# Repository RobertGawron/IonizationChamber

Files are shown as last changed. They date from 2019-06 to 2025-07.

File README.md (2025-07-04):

# Ionization Chamber (a device for measuring radioactivity levels)



## Objective

There are many ionization chamber projects online, but most (though not all) produce false positive results. It's cool when a radioactive sample is placed near the detector and the detector shows an increased radiation value, but then, if you place your hand or any non-radioactive object nearby, the readings are high too. This is because, due to high amplification, these devices pick up a lot of noise, making the measurements unreliable.

This project aims to address and eliminate this issue.

## Principle of operation

An ionization chamber is a type of radiation detector that measures ionizing radiation by detecting the charged particles (ions) produced when radiation interacts with the gas inside the chamber. The basic working principle relies on the ionization process. 

* **Radiation Interaction:** When ionizing radiation (such as alpha, beta, or gamma radiation) enters the chamber, it interacts with the gas inside, typically air. This interaction causes the gas molecules to become ionized, producing free electrons and positive ions. 
* **Electric Field:** The chamber contains two electrodes: a central anode and a surrounding cathode. A high voltage is applied between these electrodes, creating an electric field inside the chamber. 
* **Ion Collection:** The free electrons, which are negatively charged, are attracted to the positive anode, while the positively charged ions are attracted to the cathode. As these ions move toward the electrodes, they create an electrical current. 
* **Current Measurement:** The generated current is directly proportional to the number of ions produced, which in turn is related to the amount of radiation that has passed through the chamber. This current is then measured and used to calculate the intensity of the radiation.

Below is an image of the device that was assembled and tested (hardware revision 4.0). Since then, a new version has been developed but has not yet been tested. This repository, in its current state, represents the latest version. For details on the tested version, [refer to 4.0 tag](https://github.com/RobertGawron/IonizationChamber/releases/tag/4.0).  

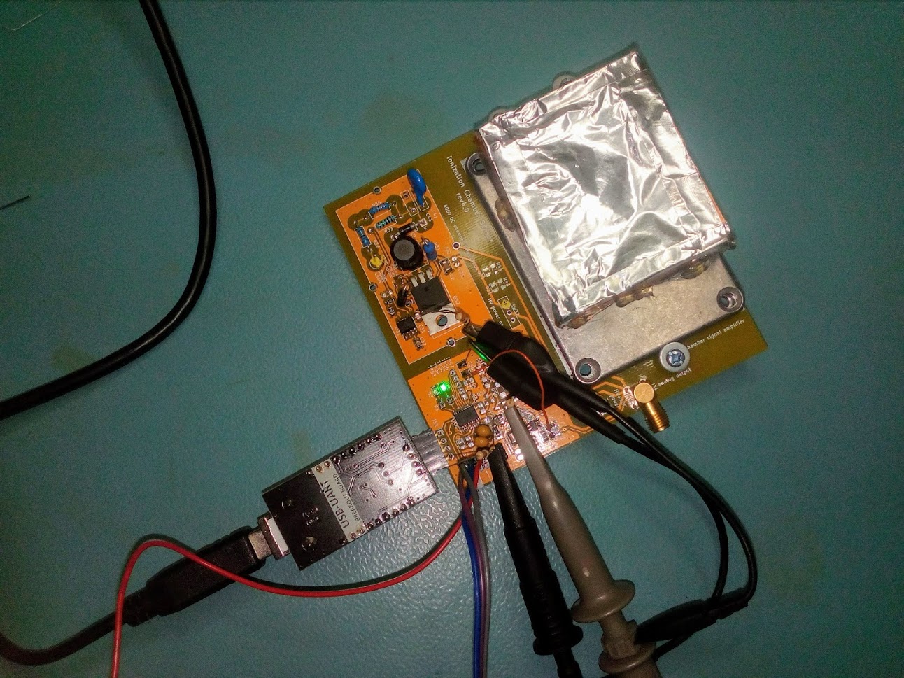
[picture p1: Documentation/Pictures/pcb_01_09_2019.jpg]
picture of device


## System architecture

It is designed in a way that the device can work remotely, e.g. no connection via USB cable to user’s PC is needed.



Remarks:
* The amplifier has three stages (the first stage is a transimpedance amplifier, not a FET transistor like most projects use).
* The ionization chamber is polarized with three 12V batteries connected in series.

## Hardware

PCB was done in KiCAD.

### Hazards

* **The battery container electrodes for chamber polarization are very close to the metal casing; the soldered electrodes should be filed down and secured with insulating tape to prevent short circuits.**
* **The device uses relatively high voltage (32V) to polarize the ionization chamber.** The electrodes of the ionization chamber should not be touched.

## Software

Measurements are collected from the COM port (tunneled over USB) by a Python script and stored in a .csv file. This file can later be parsed using R scripts to generate various diagrams, such as radioactivity changes over time, radioactivity histograms, and box plots for different samples.

measurement data flow diagram

* [Details about the firmware are available here.](./Software/Firmware/README.md)
* [Details about the acquisition software are available here.](./Software/MeasurementAcquisition/README.md)
* [Details about the measurement processing software are available here.](./Software/MeasurementAnalysis/README.md)

In the future, data from the device will be gathered and processed using the [HardwareDataLogger project](https://github.com/RobertGawron/HardwareDataLogger), which is currently in development.

## Simulation

A simple mockup was created to generate dummy test data without the need for the real device. This allows testing of the acquisition software (mainly the scripts that generate output diagrams) without requiring hardware.

[More details.](Simulation/README.md)

## DevOps

All software is developed inside a Docker container.

[More information about setting up the environment.](./Documentation/Manuals/README.md)

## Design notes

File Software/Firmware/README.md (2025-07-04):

# Architecture

Below is the sequence diagram for the firmware.

firmware main sequence diagram

firmware tick sequence diagram

# Building Firmware

Docker is used to create an isolated and reproducible work environment.

[Detailed information about setting up the environment.](../../Documentation/Manuals/README.md)

# Protocol for sending measurements via UART

## Purpose

To ensure data integrity when sending information from the ionization chamber device to the computer, a simple protocol was added to encapsulate each data or command transmission.

## Protocol details

### Definition of the message

uart frame format diagram

The field “msg length” describes the number of bytes in the “data” section.

The content of the data section in the above message is an example and may vary depending on the message ID. Currently, only one message is supported, as shown above.

### Defined message ids and message content

Currently, only one message type is defined (with ID = 1).

* Msg ID: 1 - Data from the last analog measurement of the actual value.
Msg Data Section:
    * ADC configuration
    * MSB (most significant byte) from ADC
    * LSB (least significant byte) from ADC

### CRC

The CRC is calculated by XOR-ing all bytes in the "preamble" and "data" sections.

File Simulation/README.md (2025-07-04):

# Simulation

## Purpose

This simulation spits out .csv files filled with random values that mimic a real device sending measurements to the PC over UART. It lets us exercise the data-processing scripts without having the actual hardware on hand.

We run the real Python application but swap in a stub for the low-level serial module. That way the identical codebase runs in both simulation and production-only the UART driver gets replaced.

# Usage

[Information on how to use this tool.](../Documentation/Manuals/README.md)

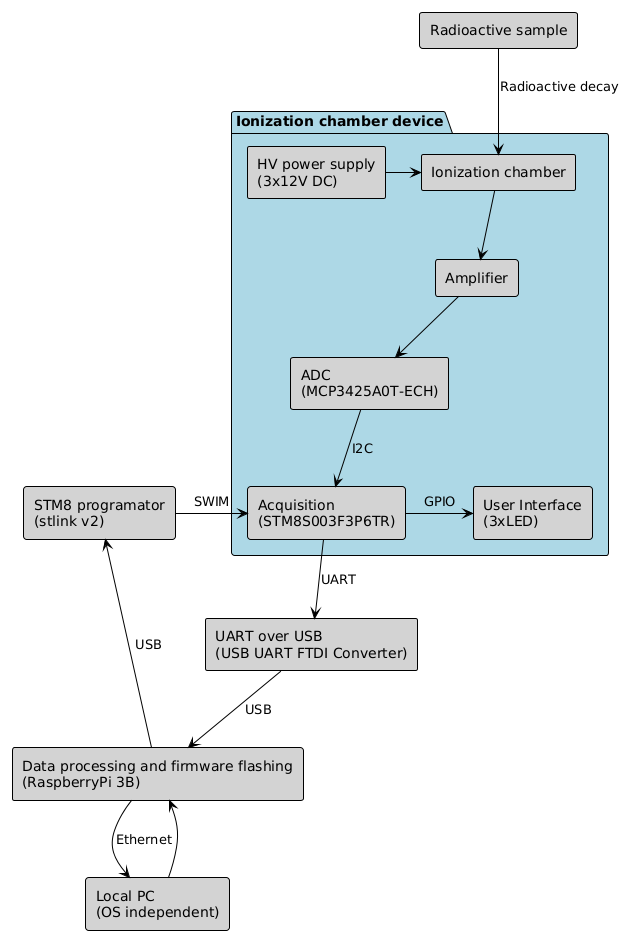
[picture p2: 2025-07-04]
Documentation/Diagrams/ArchitectureOverview-1.png

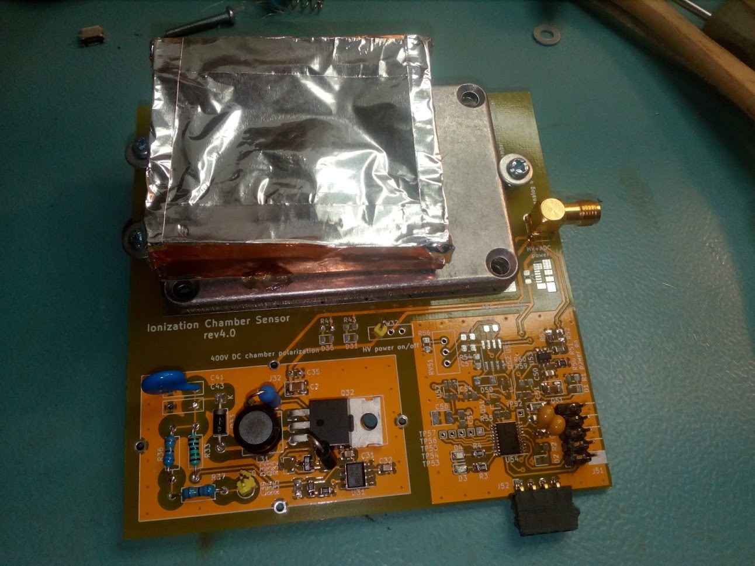
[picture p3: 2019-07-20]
Documentation/Pictures/pcb_20_07_2019.jpg

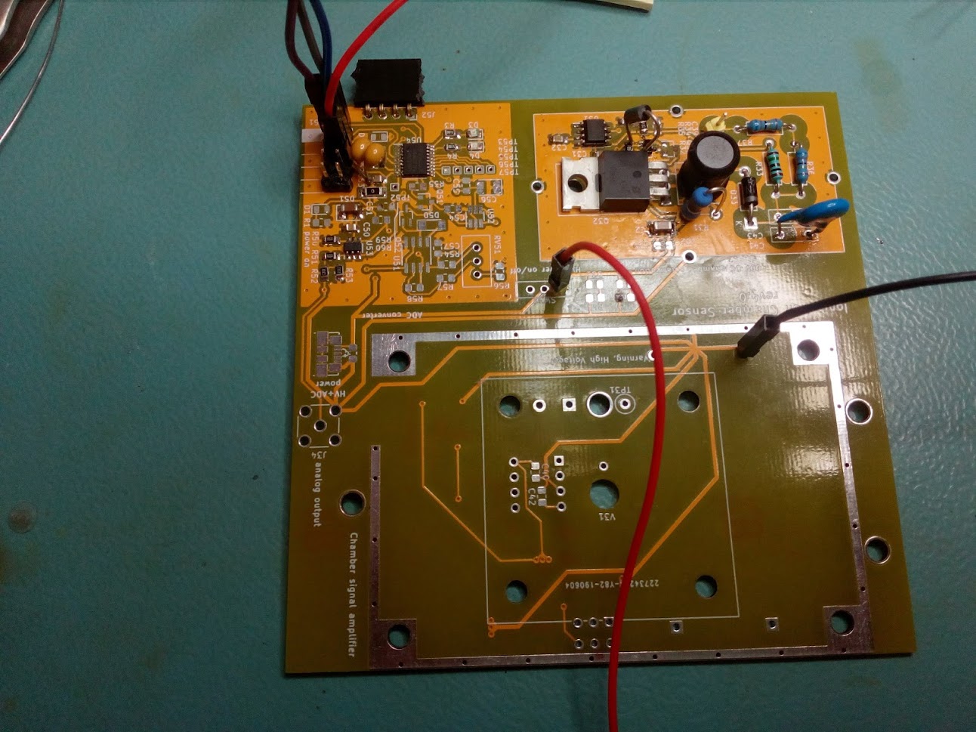
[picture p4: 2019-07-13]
Documentation/Pictures/pcb_13_07_2019.jpg

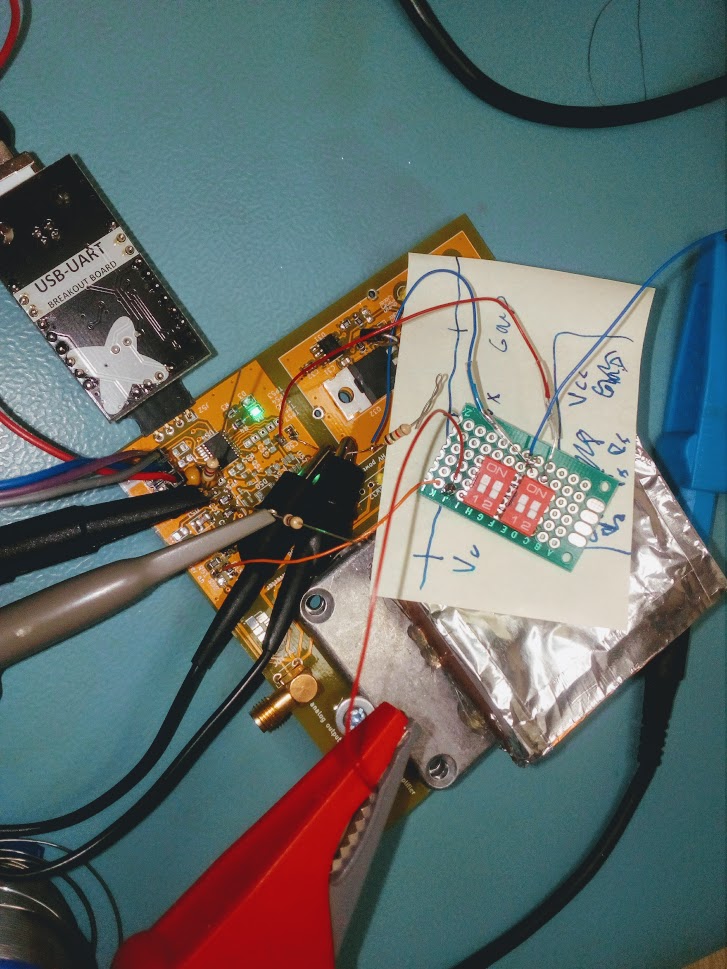
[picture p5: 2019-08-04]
Documentation/Pictures/pcb_04_08_2019.jpg

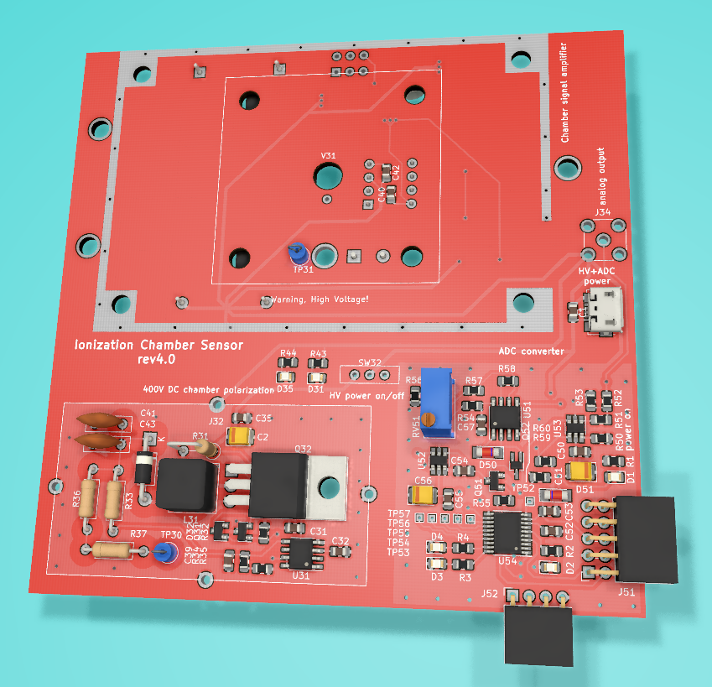
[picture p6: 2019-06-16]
Documentation/Pictures/render_26_05_2019.png

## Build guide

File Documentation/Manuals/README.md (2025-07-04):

# Toolchain

# Prerequisites

Install Docker. For Windows you need WSL installed first and some Linux image for it.

# Building, running, and stopping a Docker image

For me, using Docker in embedded systems has a key advantage: it eliminates the need for a README filled with outdated commands for setting up the development environment. In reality, such lists are rarely kept up to date (I often forget to update them myself too!). Docker solves this problem by providing a structured list of everything you need to install to get your environment up and running. But it's more than just a list - it's code, meaning it can be verified, maintained, and reused easily.

Build the Docker image by running the following command in the IonizationChamber directory. Rebuild only if the Dockerfile or docker-compose.yml changes:

docker-compose build

Start the Docker Image. Run the following command to start the Docker container:

docker-compose up -d

Log into the Docker Image:

docker-compose exec ionizationchamber bash

To log out from the Docker container, press Ctrl+D.

To stop and clean up the Docker

docker-compose down --remove-orphans

# Building firmware

Log into the Docker container (Building, running, and stopping a Docker image" section).

Run the following commands:

mkdir -p /workspace/build/firmware && cd /workspace/build/firmware 
cmake -DCMAKE_TOOLCHAIN_FILE=/workspace/Software/Firmware/sdcc-stm8.cmake -B . -S /workspace/Software/Firmware/ && cmake --build . -j$(nproc)

oneliner:

mkdir -p /workspace/build/firmware && cd /workspace/build/firmware && cmake -DCMAKE_TOOLCHAIN_FILE=/workspace/Software/Firmware/sdcc-stm8.cmake -B . -S /workspace/Software/Firmware/ && cmake --build . -j$(nproc)

The produced binary is IonizationChamber.ihx.

# Hardware flashing

For first time flashing the IC needs to be unlocked:

stm8flash -c stlinkv2 -p stm8s003f3 -u

Flashing:

stm8flash -c stlinkv2 -p stm8s003f3 -w IonizationChamber.ihx

# C Docs coverage

source /workspace/venv/bin/activate && cd /workspace/build/ && rm -rf /workspace/build/* && cmake /workspace/ && make docs

# C, Python and R Code Formatter

source /workspace/venv/bin/activate && cd /workspace/build/ && cmake /workspace/ && make style

# Firmware Unit Tests and Code Coverage

mkdir -p /workspace/build/ut && cd /workspace/build/ut
cmake -DCMAKE_BUILD_TYPE=Debug /workspace/Software/Firmware/UnitTest/
make -j$(nproc)
make run_all_tests
make coverage

oneliner:

mkdir -p /workspace/build/ut && cd /workspace/build/ut && cmake -DCMAKE_BUILD_TYPE=Debug /workspace/Software/Firmware/UnitTest/ && make -j$(nproc) && make run_all_tests  && make coverage

# C static analyze

source /workspace/venv/bin/activate && cd /workspace/build && cmake .. && make cstatic

Note: cppcheck is explicite not installed, this tool gives so much false warnings and so little actual help that it pointless to use.

# Python static analyze

source /workspace/venv/bin/activate && cd /workspace/build && cmake .. && make pystatic

# Python Unit Test and Code Coverage

source /workspace/venv/bin/activate && cd /workspace/build && cmake .. && make pycoverage

# R static analyze

source /workspace/venv/bin/activate && cd /workspace/build && cmake .. && make rstatic

# Running MeasurementAcquisition scripts

Log into the Docker container (Building, running, and stopping a Docker image" section).

Edit config.py to select the correct COM port for the Ionization Chamber.

Run the data acquisition script. It will log the Ionization Chamber's output to the screen and save it to data.csv for further processing.

python main.py

# UML generation

docker pull plantuml/plantuml-server:jetty

docker run -d -p 8080:8080 plantuml/plantuml-server:jetty

For more details:
https://plantuml.com/starting

# Simulation

source /workspace/venv/bin/activate

pip install -e /workspace/Software/MeasurementAcquisition

cd /workspace/Simulation && python3 main.py

Stop after couple of seconds by pressing Ctr+D, it will generate .cvs file with dummy data

# Credits:
* [stm8flash in Docker](https://github.com/ivankomolin/docker-stm8/blob/master/Dockerfile)

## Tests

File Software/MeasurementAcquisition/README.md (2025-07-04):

# Simulation

## Purpose

This application gathers data from the device via UART over USB and stores timestamped measurements in a .csv file for further processing.

It was developed to run on a Raspberry Pi but should work on any Linux or Windows system. One note for running it on Windows is that the name of the COM port (configured in DEVICE_ID) has a different format.

# Usage

[Information on how to use this tool can be found in the "Building, running, and stopping a Docker image" and "Running MeasurementAcquisition scripts" sections.](../DevOps/Docker/README.md)

## Architecture

The diagram below shows the **Sequence Diagram** of this application:

state diagram

Note that the application can't be stopped normally; use Ctrl+C to terminate it.

The diagram below shows the **State Diagram** of this application:

state diagram

Note that the "Failure" state is not implemented. We assume that everything works correctly all the time.

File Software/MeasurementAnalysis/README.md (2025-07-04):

# Purpose

Scripts for analyzing and visualizing radiation measurement data from ionization chamber sensor.

# Content

## Single Sample Analysis (radiation_analysis_single.R)

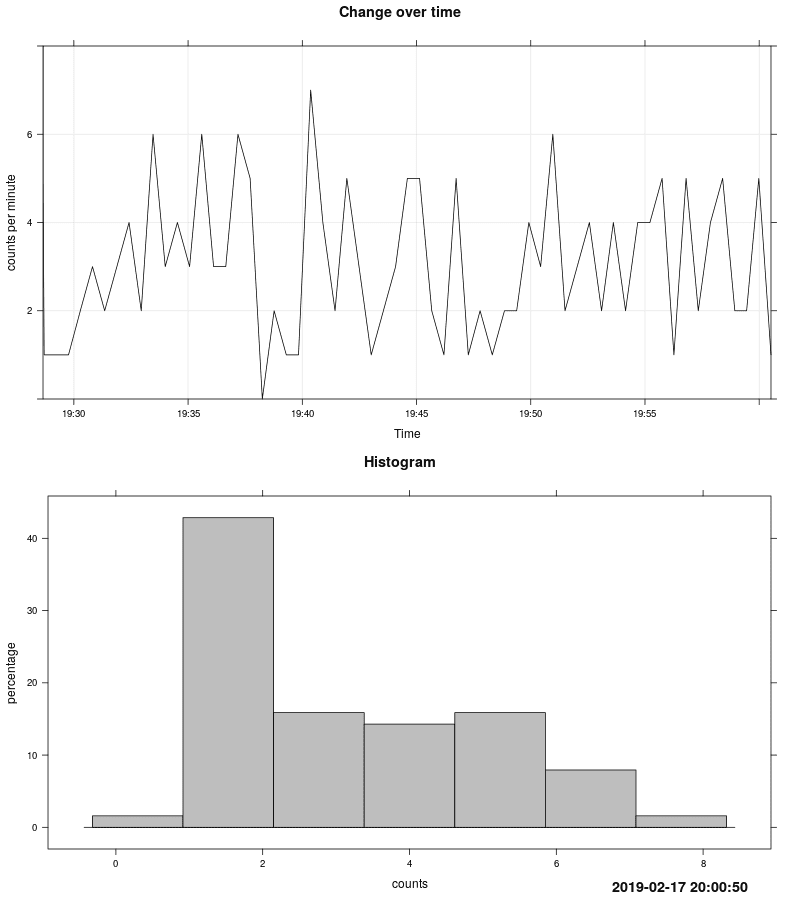
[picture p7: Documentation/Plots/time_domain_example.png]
time_domain


#### Purpose:

Analyzes a single radiation sample, producing:

Time series plot of radiation counts

Histogram of radiation distribution

#### Input

A CSV file (data.csv) with two columns:

Time: Timestamps in %Y-%m-%d %H:%M:%S.%OS format

Voltage: Measured voltage from ionization chamber

#### Output

Two image files (PNG and SVG) with the filename pattern:
radiation_analysis_single_<timestamp>.<ext>

#### Usage

Place your data in data.csv in the same directory

Run the script:

Rscript radiation_analysis_single.R

## Multi-Sample Comparison (radiation_analysis_multi.R)

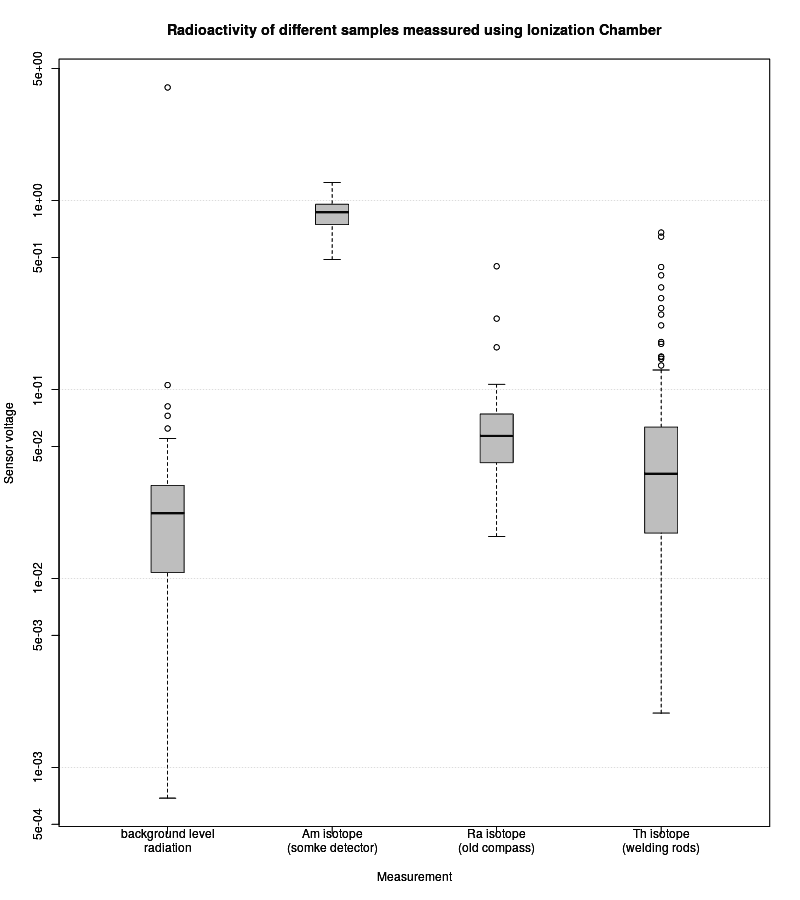
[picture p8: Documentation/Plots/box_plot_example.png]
boxplot


#### Purpose

Compares radiation levels across multiple samples using boxplots.

#### Input

Multiple CSV files (configured in the script) each containing:

Time: Timestamps (optional, used for footer)

Voltage: Radiation counts (required)

#### Output

Two image files (PNG and SVG) with the pattern:
radiation_comparison_<timestamp>.<ext>

#### Usage

Configure samples in the radiation_analysis_multi.R script (search for line shown below)

samples <- list(
  background = list(file = "DataNoSample.csv", name = "Background Radiation"),
  americium = list(file = "DataSample1.csv", name = "Am-241 (Smoke Detector)"),
  radium = list(file = "DataSample2.csv", name = "Ra-226 (Old Compass)")
)

Run the script:

Rscript radiation_analysis_multi.R

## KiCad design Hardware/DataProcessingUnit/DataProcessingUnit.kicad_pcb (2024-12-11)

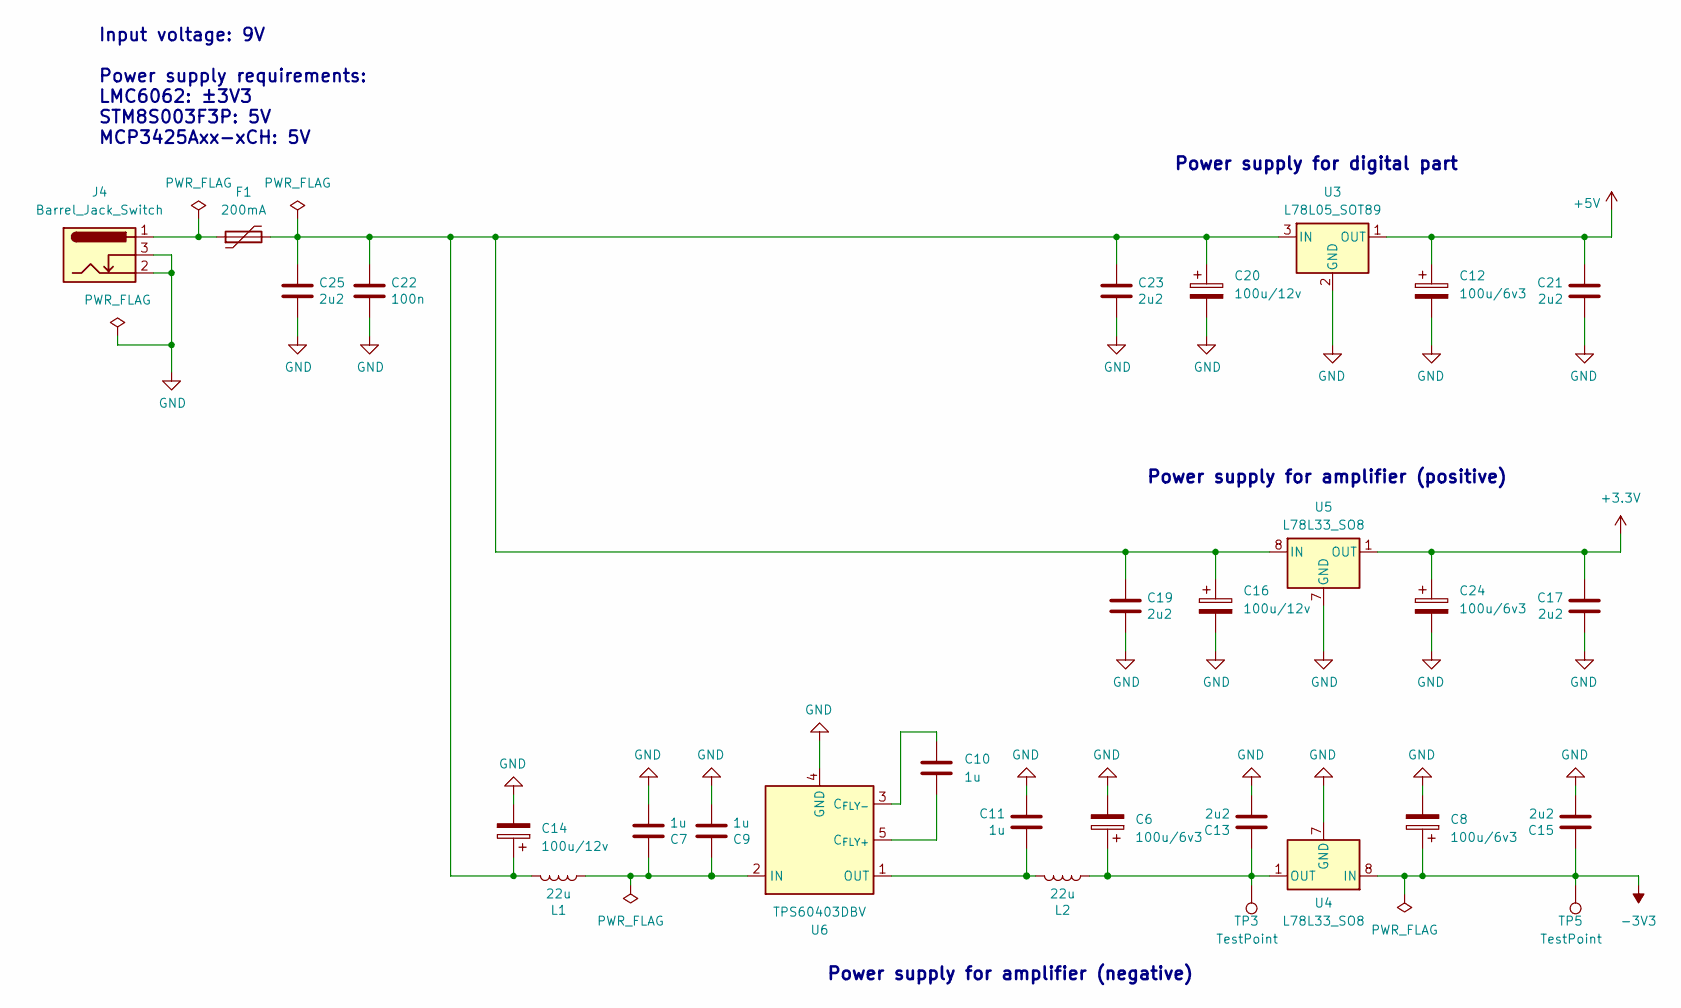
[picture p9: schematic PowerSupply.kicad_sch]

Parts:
C6, C8, C24: 100u/6v3; CP_EIA-3528-21_Kemet-B
C7, C9, C10, C11: 1u; C_0805_2012Metric
C12: 100u/6v3; CP_Elec_6.3x5.8
C13, C15, C17, C19, C21, C23, C25: 2u2; C_0805_2012Metric
C14, C16, C20: 100u/12v; CP_Elec_6.3x5.8
C22: 100n; C_0805_2012Metric
F1: 200mA; Fuse_1206_3216Metric
J4: Barrel_Jack_Switch; BarrelJack_GCT_DCJ200-10-A_Horizontal
L1, L2: 22u; L_7.3x7.3_H3.5
TP3, TP5: TestPoint; TestPoint_Pad_D1.0mm
U3: L78L05_SOT89; SOT-89-3
U4, U5: L78L33_SO8; SOIC-8_3.9x4.9mm_P1.27mm
U6: TPS60403DBV; SOT-23-5

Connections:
+3.3V: C17.1, C24.1, U5.1 (OUT); also elsewhere on the board
+5V: C12.1, C21.1, U3.1 (OUT); also elsewhere on the board
-3V3: C8.1, C15.1, TP5.1, U4.8 (IN); also elsewhere on the board
GND: C6.2, C7.2, C8.2, C9.2, C11.2, C12.2, C13.2, C14.2, C15.2, C16.2, C17.2, C19.2, C20.2, C21.2, C22.2, C23.2, C24.2, C25.2, J4.2, J4.3, U3.2 (GND), U4.2 (GND), U4.3 (GND), U4.6 (GND), U4.7 (GND), U5.2 (GND), U5.3 (GND), U5.6 (GND), U5.7 (GND), U6.4 (GND); also elsewhere on the board
unnamed: F1.1, J4.1
unnamed: C14.1, C16.1, C19.1, C20.1, C22.1, C23.1, C25.1, F1.2, L1.2, U3.3 (IN), U5.8 (IN)
unnamed: C6.1, C13.1, L2.1, TP3.1, U4.1 (OUT)
unnamed: C10.2, U6.5 (C_{FLY+})
unnamed: C10.1, U6.3 (C_{FLY-})
unnamed: C7.1, C9.1, L1.1, U6.2 (IN)
unnamed: C11.1, L2.2, U6.1 (OUT)

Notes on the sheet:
Power supply for amplifier (negative)
Power supply for amplifier (positive)
Power supply for digital part
Input voltage: 9V Power supply requirements: LMC6062: ±3V3 STM8S003F3P: 5V MCP3425Axx-xCH: 5V

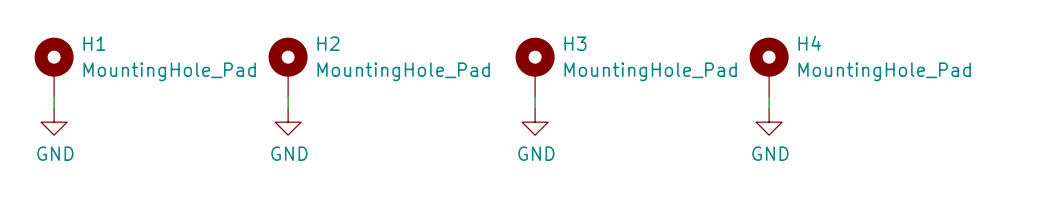
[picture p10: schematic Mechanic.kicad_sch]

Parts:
H1, H2, H3, H4: MountingHole_Pad; MountingHole_3.5mm_Pad

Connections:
GND: H1.1, H2.1, H3.1, H4.1; also elsewhere on the board

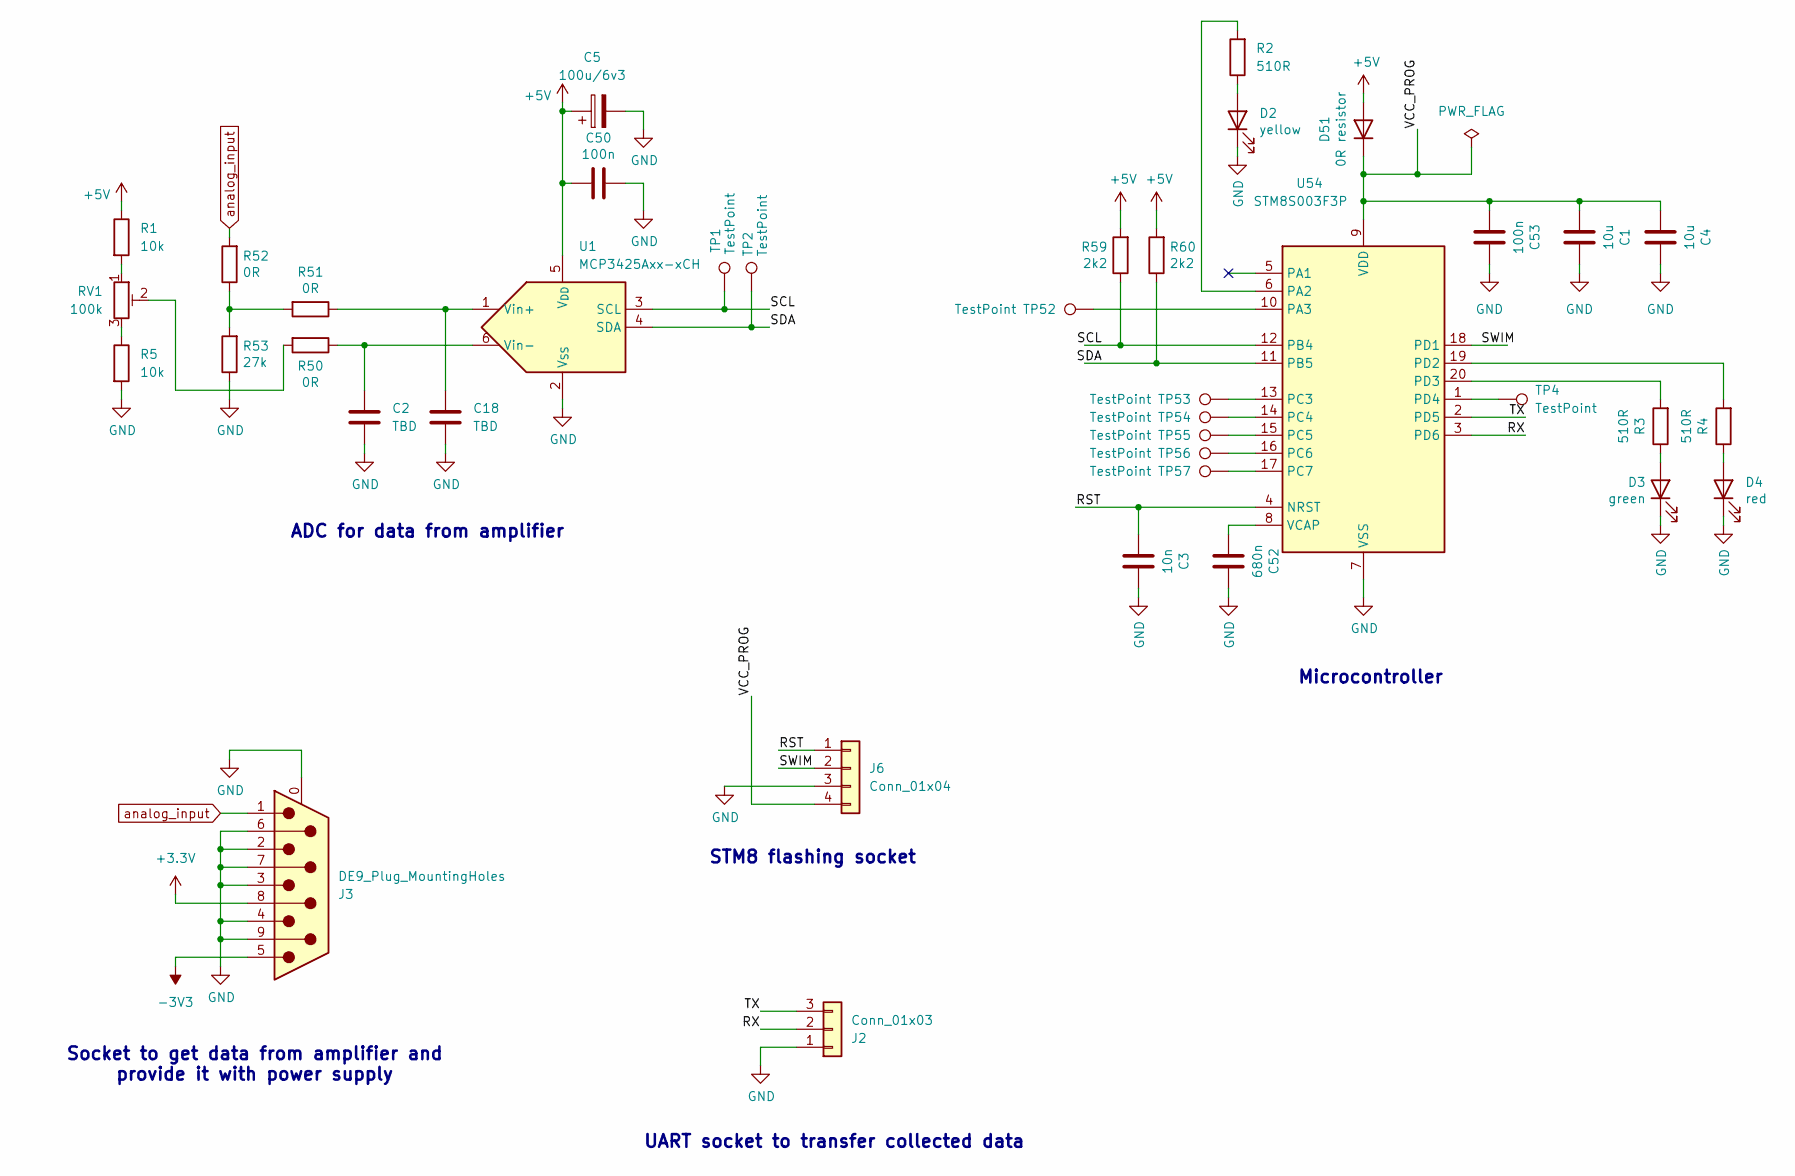
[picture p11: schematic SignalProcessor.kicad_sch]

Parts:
C1, C4: 10u; C_0805_2012Metric
C2, C18: TBD; C_0805_2012Metric
C3: 10n; C_0805_2012Metric
C5: 100u/6v3; CP_EIA-3528-21_Kemet-B
C50, C53: 100n; C_0805_2012Metric
C52: 680n; C_0805_2012Metric
D2: yellow; LED_0805_2012Metric
D3: green; LED_0805_2012Metric
D4: red; LED_0805_2012Metric
D51: 0R resistor; D_MiniMELF
J2: Conn_01x03; PinSocket_1x03_P2.54mm_Horizontal
J3: DE9_Plug_MountingHoles; DSUB-9_Male_Vertical_P2.77x2.84mm_MountingHoles
J6: Conn_01x04; PinSocket_1x04_P2.54mm_Horizontal
R1, R5: 10k; R_0805_2012Metric
R2, R3, R4: 510R; R_0805_2012Metric
R50, R51, R52: 0R; R_0805_2012Metric
R53: 27k; R_0805_2012Metric
R59, R60: 2k2; R_0805_2012Metric
RV1: 100k; Potentiometer_Bourns_3296W_Vertical
TP1, TP2, TP4, TP52, TP53, TP54, TP55, TP56, TP57: TestPoint; TestPoint_Pad_D1.0mm
U1: MCP3425Axx-xCH; SOT-23-6
U54: STM8S003F3P; TSSOP-20_4.4x6.5mm_P0.65mm

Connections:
+3.3V: J3.8; also elsewhere on the board
+5V: C5.1, C50.2, D51.2 (A), R1.1, R59.2, R60.2, U1.5 (V_{DD}); also elsewhere on the board
-3V3: J3.5; also elsewhere on the board
/SignalProcessor/RST: C3.2, J6.1, U54.4 (NRST)
/SignalProcessor/RX: J2.2, U54.3 (PD6)
/SignalProcessor/SCL: R59.1, TP1.1, U1.3 (SCL), U54.12 (PB4)
/SignalProcessor/SDA: R60.1, TP2.1, U1.4 (SDA), U54.11 (PB5)
/SignalProcessor/SWIM: J6.2, U54.18 (PD1)
/SignalProcessor/TX: J2.3, U54.2 (PD5)
/SignalProcessor/VCC_PROG: C1.2, C4.2, C53.2, D51.1 (K), J6.4, U54.9 (VDD)
GND: C1.1, C2.2, C3.1, C4.1, C5.2, C18.2, C50.1, C52.1, C53.1, D2.1 (K), D3.1 (K), D4.1 (K), J2.1, J3.0 (PAD), J3.2, J3.3, J3.4, J3.6, J3.7, J3.9, J6.3, R5.2, R53.1, U1.2 (V_{SS}), U54.7 (VSS); also elsewhere on the board
unnamed: D2.2 (A), R2.1
unnamed: D3.2 (A), R3.1
unnamed: D4.2 (A), R4.1
unnamed: R1.2, RV1.1
unnamed: R5.1, RV1.3
unnamed: R50.2, RV1.2
unnamed: R51.2, R52.1, R53.2
unnamed: C18.1, R51.1, U1.1 (Vin+)
unnamed: C2.1, R50.1, U1.6 (Vin-)
unnamed: R2.2, U54.6 (PA2)
unnamed: TP52.1, U54.10 (PA3)
unnamed: TP53.1, U54.13 (PC3)
unnamed: TP54.1, U54.14 (PC4)
unnamed: TP55.1, U54.15 (PC5)
unnamed: TP56.1, U54.16 (PC6)
unnamed: TP57.1, U54.17 (PC7)
unnamed: R4.2, U54.19 (PD2)
unnamed: R3.2, U54.20 (PD3)
unnamed: TP4.1, U54.1 (PD4)
unnamed: C52.2, U54.8 (VCAP)
analog_input: J3.1, R52.2

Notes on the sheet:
Socket to get data from amplifier and provide it with power supply
Microcontroller
ADC for data from amplifier
STM8 flashing socket
UART socket to transfer collected data

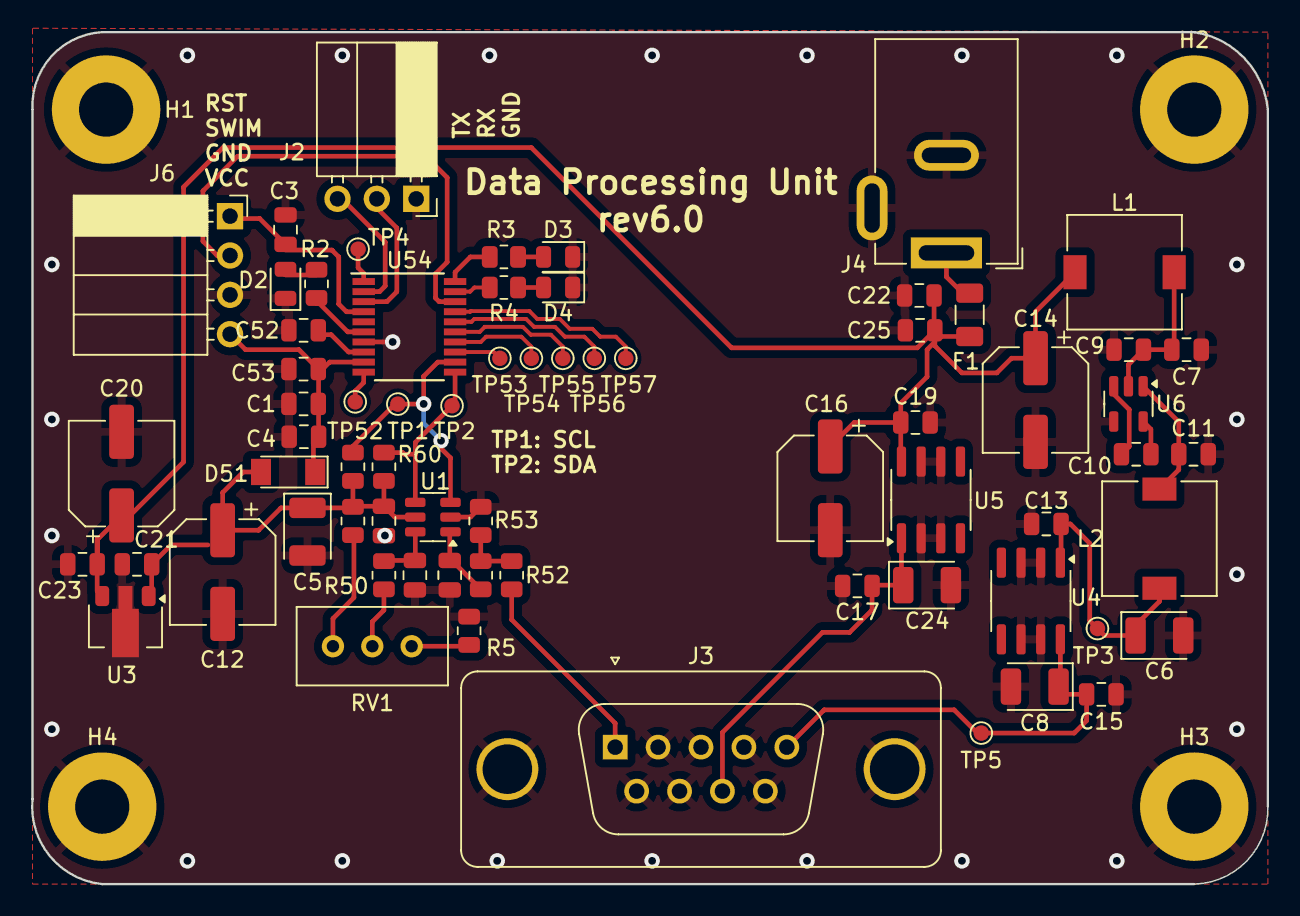
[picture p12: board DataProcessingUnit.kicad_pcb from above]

Board: 2 copper layers, 79.8 x 55.0 mm, 72 parts (0 on the bottom side), 39 nets.

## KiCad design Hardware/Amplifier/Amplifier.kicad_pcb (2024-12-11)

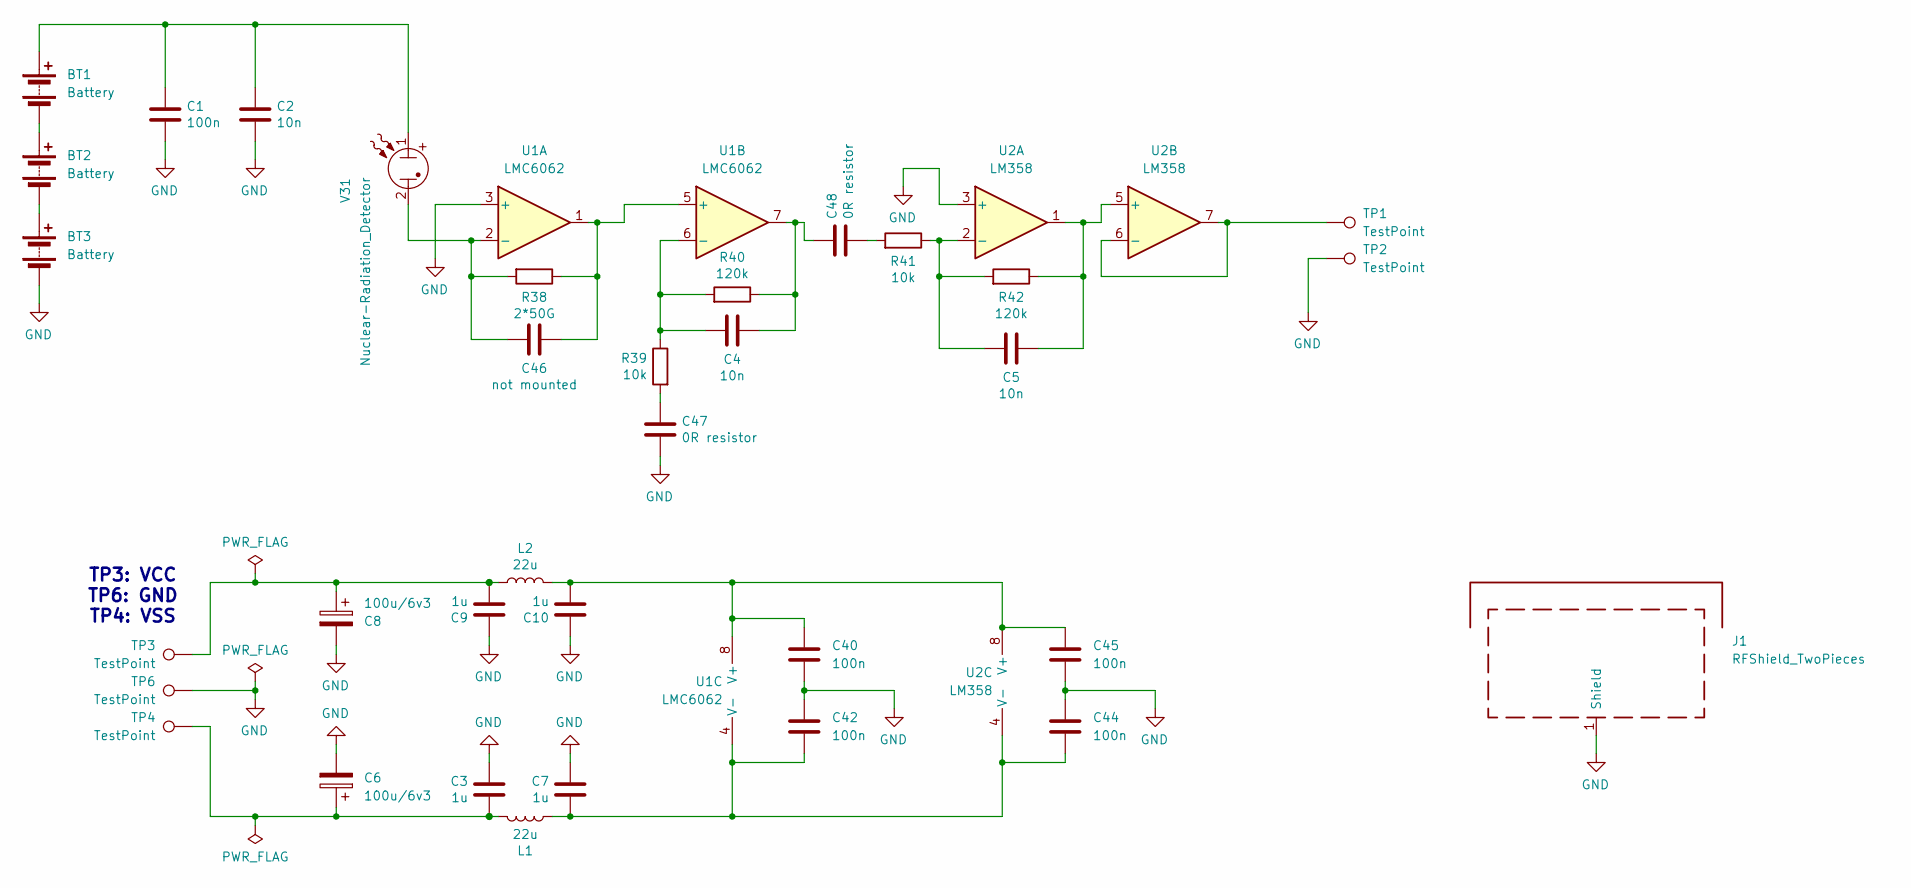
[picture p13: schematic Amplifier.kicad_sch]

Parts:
BT1, BT2, BT3: Battery; AAAAPCBHolder
C1, C40, C42, C44, C45: 100n; C_0805_2012Metric
C2, C4, C5: 10n; C_0805_2012Metric
C3, C7, C9, C10: 1u; C_0805_2012Metric
C6, C8: 100u/6v3; CP_EIA-3528-21_Kemet-B
C46: not mounted; C_0805_2012Metric
C47, C48: 0R resistor; C_0805_2012Metric
J1: RFShield_TwoPieces; IonizationChamberShield
L1, L2: 22u; L_7.3x7.3_H3.5
R38: 2*50G; R_0805_2012Metric_Pad1.15x1.40mm_HandSolder
R39, R41: 10k; R_0805_2012Metric
R40, R42: 120k; R_0805_2012Metric
TP1, TP2, TP3, TP4, TP6: TestPoint; TestPoint_Loop_D2.60mm_Drill0.9mm_Beaded
U1: LMC6062; DIP-8_W7.62mm
U2: LM358; SO-8_3.9x4.9mm_P1.27mm
V31: Nuclear-Radiation_Detector; IonizationChamberSensor

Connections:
GND: BT3.2 (-), C1.2, C2.2, C3.2, C6.2, C7.2, C8.2, C9.2, C10.2, C40.2, C42.2, C44.2, C45.1, C47.2, J1.1 (Shield), TP2.1, TP6.1, U1.3 (+), U2.3 (+)
unnamed: BT1.1 (+), C1.1, C2.1, V31.1
unnamed: BT1.2 (-), BT2.1 (+)
unnamed: BT2.2 (-), BT3.1 (+)
unnamed: C3.1, C6.1, L1.2, TP4.1
unnamed: C4.2, C48.1, R40.1, U1.7
unnamed: C8.1, C9.1, L2.2, TP3.1
unnamed: C47.1, R39.2
unnamed: C48.2, R41.2
unnamed: C46.2, R38.2, U1.2 (-), V31.2
unnamed: C46.1, R38.1, U1.1, U1.5 (+)
unnamed: C4.1, R39.1, R40.2, U1.6 (-)
unnamed: C10.1, C40.1, C45.2, L2.1, U1.8 (V+), U2.8 (V+)
unnamed: C7.1, C42.1, C44.1, L1.1, U1.4 (V-), U2.4 (V-)
unnamed: C5.1, R41.1, R42.2, U2.2 (-)
unnamed: C5.2, R42.1, U2.1, U2.5 (+)
unnamed: TP1.1, U2.6 (-), U2.7

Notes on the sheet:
TP3: VCC TP6: GND TP4: VSS

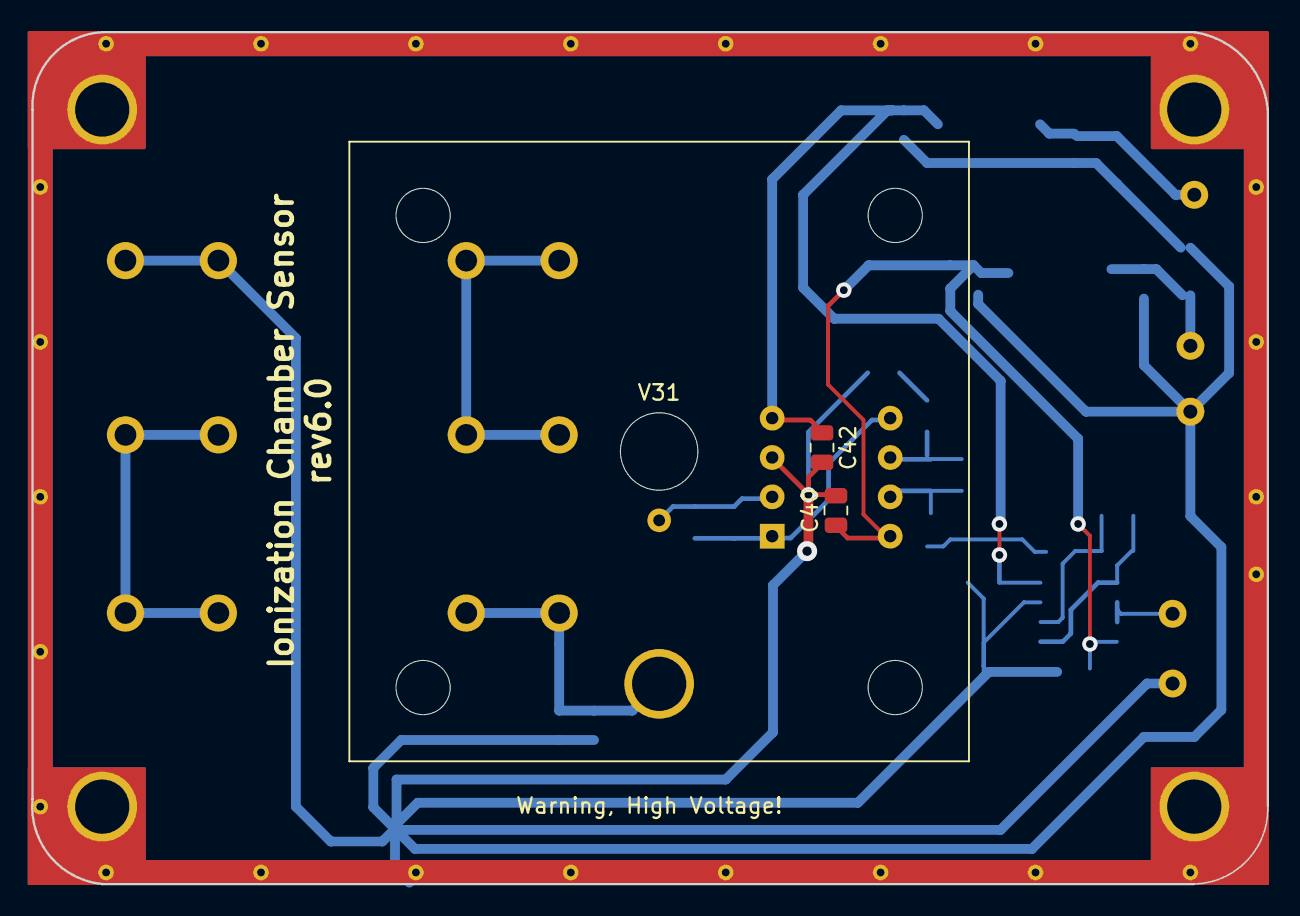
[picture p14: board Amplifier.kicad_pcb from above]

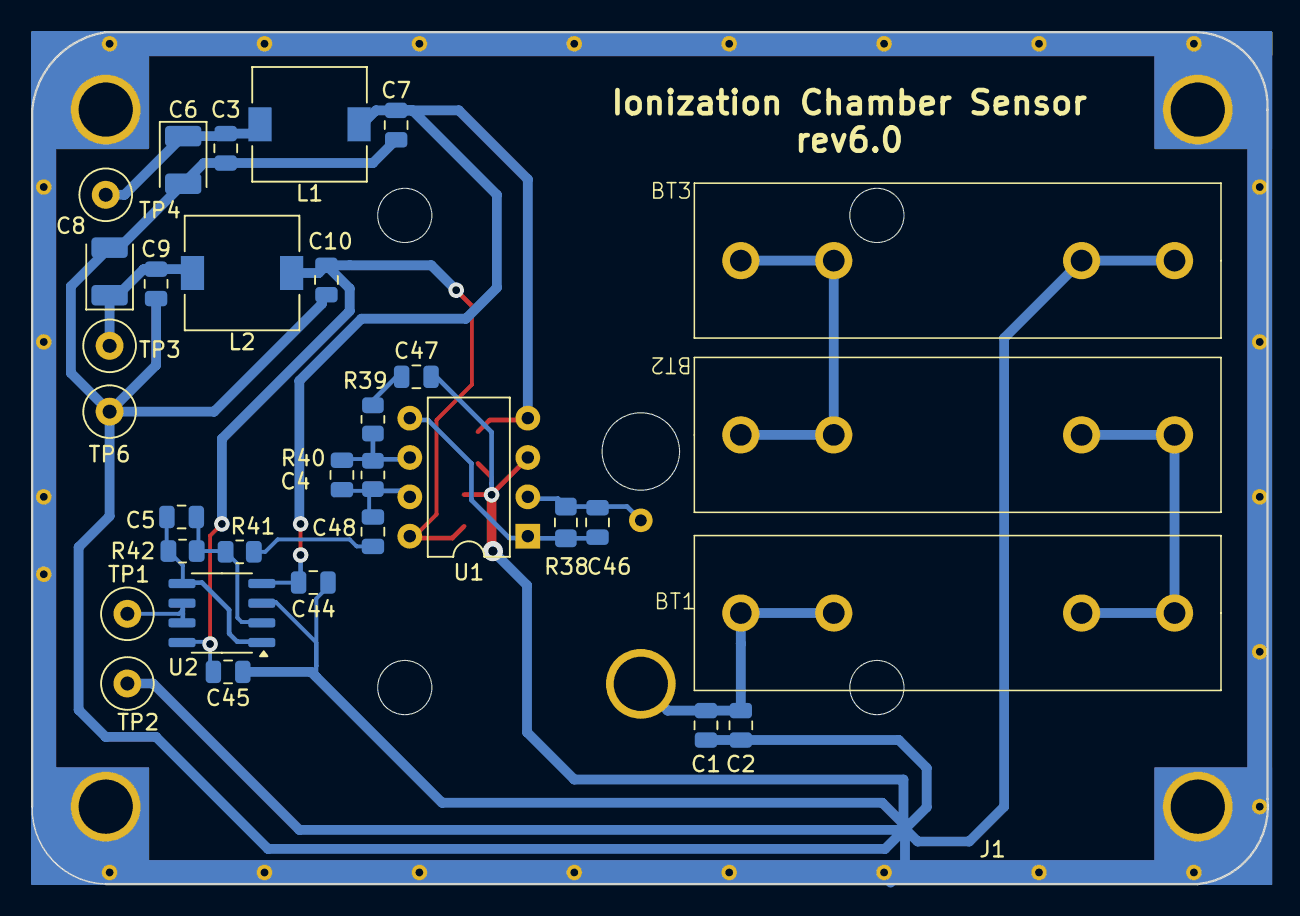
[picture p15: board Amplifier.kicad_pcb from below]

Board: 2 copper layers, 79.8 x 55.0 mm, 36 parts (33 on the bottom side), 17 nets.

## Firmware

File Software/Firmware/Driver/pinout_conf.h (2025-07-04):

#ifndef pinout_conf_h
#define pinout_conf_h

/**
 * @file pinout_conf.h
 * @brief Hardware pin configuration definitions.
 *
 * Defines GPIO port and pin mappings for peripherals including UART, LEDs, and
 * I2C.
 */

/**
 * @name UART Configuration
 * @{
 */
#define PORT_UART GPIOD   /**< UART peripheral GPIO port */
#define PIN_TX GPIO_PIN_5 /**< UART transmit pin number */
#define PIN_RX GPIO_PIN_6 /**< UART receive pin number */
/** @} */

/**
 * @name LED Configuration
 * @{
 */
#define PORT_LED GPIOD           /**< LED GPIO port */
#define PIN_LED_GREEN GPIO_PIN_2 /**< Green LED pin number */
#define PIN_LED_RED GPIO_PIN_3   /**< Red LED pin number */
/** @} */

/**
 * @name I2C Configuration
 * @{
 */
#define PORT_I2C GPIOB         /**< I2C peripheral GPIO port */
#define PIN_I2C_SCL GPIO_PIN_4 /**< I2C clock line pin */
#define PIN_I2C_SDA GPIO_PIN_5 /**< I2C data line pin */
/** @} */

#endif

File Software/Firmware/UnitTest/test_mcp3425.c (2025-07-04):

#include <stdarg.h>
#include <stddef.h>
#include <setjmp.h> // NOLINT(misc-include-cleaner), needed by <cmocka.h>
#include <cmocka.h>
#include <stdint.h>

// Include production code
#include "mcp3425.h"
#include "stm8s_i2c.h"
#include "stm8s_gpio.h"

#include "stm8s.h"

// =============================================================================
// TEST CONFIGURATION
// =============================================================================

/**
 * @def I2C_MASTER_ADDRESS
 * @brief I2C master address for testing
 */
#define I2C_MASTER_ADDRESS 0x10

// =============================================================================
// MOCK STATE TRACKING
// =============================================================================
/**
 * @var i2c_bus_busy
 * @brief Tracks I2C bus busy status
 */
static bool i2c_bus_busy = FALSE;

/**
 * @var i2c_last_sent_data
 * @brief Stores the last byte sent via I2C
 */
static uint8_t i2c_last_sent_data = 0;

#define RECEIVE_DATA_LEN 8
/**
 * @var i2c_receive_data
 * @brief Buffer for simulated I2C receive data
 */
static uint8_t i2c_receive_data[RECEIVE_DATA_LEN] = {0};

/**
 * @var i2c_receive_index
 * @brief Index for reading from receive buffer
 */
static uint8_t i2c_receive_index = 0;

/**
 * @var i2c_event_status
 * @brief Simulates I2C event status register
 */
static uint8_t i2c_event_status = 0;

// =============================================================================
// MOCK FUNCTION IMPLEMENTATIONS
// =============================================================================
/**
 * @brief Mock implementation of GPIO_Init
 *
 * Stub function to satisfy linker requirements.
 *
 * @param GPIOx GPIO port pointer
 * @param GPIO_Pin Pin selection
 * @param GPIO_Mode Pin mode configuration
 */
void GPIO_Init(
    GPIO_TypeDef *    GPIOx,
    GPIO_Pin_TypeDef GPIO_Pin,
    GPIO_Mode_TypeDef GPIO_Mode)
{
    (void)GPIOx;
    (void)GPIO_Pin;
    (void)GPIO_Mode;
}

/**
 * @brief Mock implementation of I2C_DeInit
 *
 * Resets all I2C mock state variables to default values.
 */
void I2C_DeInit(
    void)
{
    i2c_bus_busy = FALSE;
    i2c_last_sent_data = 0;
    i2c_receive_index = 0;
    i2c_event_status = 0;
}

/**
 * @brief Mock implementation of I2C_Init
 *
 * Verifies I2C initialization parameters.
 *
 * @param OutputClockFrequencyHz Desired I2C clock frequency
 * @param OwnAddress Master device address
 * @param I2C_DutyCycle I2C duty cycle mode
 * @param Ack Acknowledge enable/disable
 * @param AddMode Addressing mode
 * @param InputClockFrequencyMHz Input clock frequency in MHz
 */
void I2C_Init(
    uint32_t OutputClockFrequencyHz,
    uint16_t OwnAddress,
    I2C_DutyCycle_TypeDef I2C_DutyCycle,
    I2C_Ack_TypeDef Ack,
    I2C_AddMode_TypeDef AddMode,
    uint8_t InputClockFrequencyMHz)
{
    check_expected(OutputClockFrequencyHz);
    check_expected(OwnAddress);
    check_expected(I2C_DutyCycle);
    check_expected(Ack);
    check_expected(AddMode);
    check_expected(InputClockFrequencyMHz);
}

/**
 * @brief Mock implementation of I2C_Cmd
 *
 * Verifies I2C enable/disable commands.
 *
 * @param NewState ENABLE or DISABLE command
 */
void I2C_Cmd(
    FunctionalState NewState)
{
    check_expected(NewState);
}

/**
 * @brief Mock implementation of I2C_GenerateSTART
 *
 * Simulates START condition generation and updates bus state.
 *
 * @param NewState ENABLE to generate START condition
 */
void I2C_GenerateSTART(
    FunctionalState NewState)
{
    if(NewState == ENABLE)
    {
        i2c_event_status |= I2C_EVENT_MASTER_MODE_SELECT;
        i2c_bus_busy = TRUE;
    }
}

/**
 * @brief Mock implementation of I2C_CheckEvent
 *
 * Simulates I2C event status checking.
 *
 * @param I2C_Event Event to check
 * @return ErrorStatus SUCCESS if event occurred, ERROR otherwise
 */
ErrorStatus I2C_CheckEvent(
    I2C_Event_TypeDef I2C_Event)
{
    return (i2c_event_status & I2C_Event) ? SUCCESS : ERROR;
}

/**
 * @brief Mock implementation of I2C_Send7bitAddress
 *
 * Verifies address transmission and simulates address ACK event.
 *
 * @param Address Slave address to send
 * @param Direction Transmission direction (TX/RX)
 */
void I2C_Send7bitAddress(
    uint8_t Address,
    I2C_Direction_TypeDef Direction)
{
    check_expected(Address);
    check_expected(Direction);

    if(Direction == I2C_DIRECTION_TX)
    {
        i2c_event_status |= I2C_EVENT_MASTER_TRANSMITTER_MODE_SELECTED;
    }
    else
    {
        i2c_event_status |= I2C_EVENT_MASTER_RECEIVER_MODE_SELECTED;
    }
}

/**
 * @brief Mock implementation of I2C_SendData
 *
 * Stores sent data and simulates byte transmission event.
 *
 * @param Data Byte to send
 */
void I2C_SendData(
    uint8_t Data)
{
    i2c_last_sent_data = Data;
    i2c_event_status |= I2C_EVENT_MASTER_BYTE_TRANSMITTED;
    check_expected(Data);
}

/**
 * @brief Mock implementation of I2C_GenerateSTOP
 *
 * Simulates STOP condition generation and resets bus state.
 *
 * @param NewState ENABLE to generate STOP condition
 */
void I2C_GenerateSTOP(
    FunctionalState NewState)
{
    if(NewState == ENABLE)
    {
        i2c_bus_busy = FALSE;
        i2c_event_status = 0;
    }
}

/**
 * @brief Mock implementation of I2C_GetFlagStatus
 *
 * Simulates I2C flag status checking.
 *
 * @param I2C_Flag Flag to check
 * @return FlagStatus SET if flag is set, RESET otherwise
 */
FlagStatus I2C_GetFlagStatus(
    I2C_Flag_TypeDef I2C_Flag)
{
    if(I2C_Flag == I2C_FLAG_BUSBUSY)
    {
        return i2c_bus_busy ? SET : RESET;
    }
    return RESET;
}

/**
 * @brief Mock implementation of I2C_ReceiveData
 *
 * Simulates data reception from I2C bus.
 *
 * @return uint8_t Received data byte
 */
uint8_t I2C_ReceiveData(
    void)
{
    if(i2c_receive_index < sizeof(i2c_receive_data))
    {
        return i2c_receive_data[i2c_receive_index++];
    }
    return 0;
}

/**
 * @brief Mock implementation of I2C_AcknowledgeConfig
 *
 * Stub function to satisfy linker requirements.
 *
 * @param Ack ACK configuration
 */
void I2C_AcknowledgeConfig(
    I2C_Ack_TypeDef Ack)
{
    (void)Ack;
}

/**
 * @brief Mock implementation of CLK_GetClockFreq
 *
 * Simulates clock frequency retrieval.
 *
 * @return uint32_t Current clock frequency
 */
uint32_t CLK_GetClockFreq(
    void)
{
    return (uint32_t)mock(); // Use mock() to return expected value
}

// =============================================================================
// TEST CASES
// =============================================================================
/**
 * @brief Tests MCP3425 initialization sequence
 *
 * Verifies that the MCP3425 initialization:
 * 1. Retrieves the correct system clock frequency
 * 2. Configures I2C peripheral with correct parameters:
 *    - 100kHz output clock
 *    - 7-bit addressing mode
 *    - Standard duty cycle
 *    - Acknowledge enabled
 * 3. Enables the I2C peripheral
 *
 * @param state CMocka state object (unused)
 */
static void test_Init_ConfiguresGPIOAndI2C(
    void **state)
{
    (void)state;

    // 1. Set clock frequency expectation
    will_return(CLK_GetClockFreq, 16000000); // 16MHz clock

    // 2. Set I2C_Init expectations
    expect_value(I2C_Init, OutputClockFrequencyHz, 100000);
    expect_value(I2C_Init, OwnAddress, I2C_MASTER_ADDRESS);
    expect_value(I2C_Init, I2C_DutyCycle, I2C_DUTYCYCLE_2);
    expect_value(I2C_Init, Ack, I2C_ACK_CURR);
    expect_value(I2C_Init, AddMode, I2C_ADDMODE_7BIT);
    expect_value(I2C_Init, InputClockFrequencyMHz, 16); // 16MHz / 1,000,000

    // 3. Set I2C_Cmd expectation
    expect_value(I2C_Cmd, NewState, ENABLE);

    // Execute function under test
    mcp3425_init();
}

// =============================================================================
// TEST RUNNER
// =============================================================================
/**
 * @brief Test runner entry point
 *
 * Executes the MCP3425 initialization test:
 * 1. Initializes the CMocka test environment
 * 2. Runs the I2C configuration test
 *
 * @return int Number of failed tests (0 if all pass)
 */
int main(
    void)
{
    const struct CMUnitTest tests[] = {
        cmocka_unit_test(test_Init_ConfiguresGPIOAndI2C)
    };

    return cmocka_run_group_tests(tests, NULL, NULL);
}

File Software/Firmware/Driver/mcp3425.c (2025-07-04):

/*
 * mcp3425.c — Driver for the MCP3425 16‑bit I2C ADC
 * Target MCU : STM8S003F3P6 (SDCC)
 *
 */

#include "mcp3425.h"
#include "pinout_conf.h"
#include "stm8s.h"
#include "stm8s_clk.h"
#include "stm8s_gpio.h"
#include "stm8s_i2c.h"

#include <stdint.h>
#include <stdbool.h>

/* -------------------------------------------------------------------------
 * I2C addresses & speed
 * -------------------------------------------------------------------------*/
#define I2C_MASTER_ADDRESS        0x10U                /* our 7‑bit address */
#define I2C_SLAVE_ADDRESS         0x68U                /* MCP3425 address   */
#define I2C_SPEED_STANDARD_HZ     100000UL             /* 100 kHz SCL       */
#define HZ_TO_MHZ(freq_hz)        ((uint8_t)((freq_hz) / 1000000UL))

/* -------------------------------------------------------------------------
 * MCP3425 configuration bits
 * -------------------------------------------------------------------------*/
#define MCP3425_RDY_BIT   (1U << 7)  /* 1 = conversion not ready            */
#define MCP3425_MODE_BIT  (1U << 4)  /* 1 = one‑shot; 0 = continuous        */
#define MCP3425_SPS_BIT   (1U << 3)  /* 1 = 16‑bit @ 15 SPS                 */
#define MCP3425_GAIN_BIT  (0U)       /* 00 = gain ×1                        */

#define MCP3425_CONFIG (MCP3425_RDY_BIT | MCP3425_MODE_BIT | MCP3425_SPS_BIT | MCP3425_GAIN_BIT)

/* -------------------------------------------------------------------------
 * Misc. constants
 * -------------------------------------------------------------------------*/
#define I2C_TIMEOUT                 10000UL             /* loop-cycle timeout */

/* -------------------------------------------------------------------------
 * Busy‑wait macro with timeout
 * -------------------------------------------------------------------------*/
#define BUSY_AWAIT_CONDITION(cond, cnt, max, on_to) do {\
            (cnt) = (uint16_t)(max);\
            while (!(cond)) {\
                if (--(cnt) == 0U) {\
                    on_to;\
                }\
            }\
} while (0)

/* Private prototypes */
static void GPIO_setup(void);
static void I2C_setup(void);
static bool write_config(uint8_t config);
static AcqResult_t read_result(uint8_t *msb, uint8_t *lsb, uint8_t *conf);

/* -------------------------------------------------------------------------
 * Public API
 * -------------------------------------------------------------------------*/
void mcp3425_init(void)
{
    GPIO_setup();
    I2C_setup();
}

AcqResult_t mcp3425_get_value(MeasurementBytes_t *measurement)
{
    if (!write_config(MCP3425_CONFIG))
    {
        return ACQ_ERROR; // bus or timeout failure
    }

    return read_result(&measurement->msb, &measurement->lsb, &measurement->conf);
}

/* -------------------------------------------------------------------------
 * Private Functions
 * -------------------------------------------------------------------------*/
static void GPIO_setup(void)
{
    GPIO_Init(PORT_I2C, PIN_I2C_SCL, GPIO_MODE_OUT_OD_HIZ_FAST);
    GPIO_Init(PORT_I2C, PIN_I2C_SDA, GPIO_MODE_OUT_OD_HIZ_FAST);
}

static void I2C_setup(void)
{
    /* Enable the I2C peripheral clock is done in clk_conf_init() */

    I2C_DeInit();

    I2C_Init(I2C_SPEED_STANDARD_HZ,
        I2C_MASTER_ADDRESS,
        I2C_DUTYCYCLE_2,
        I2C_ACK_CURR,
        I2C_ADDMODE_7BIT,
        HZ_TO_MHZ(CLK_GetClockFreq()));

    I2C_Cmd(ENABLE);
}

static bool write_config(const uint8_t config)
{
    uint16_t timeout_counter = I2C_TIMEOUT;

    while (I2C_GetFlagStatus(I2C_FLAG_BUSBUSY))
    {
        if (--timeout_counter == 0)
        {
            //i2c_recover();  // todo : implement recovery function
            return false;
        }
    }

    I2C_GenerateSTART(ENABLE);
    BUSY_AWAIT_CONDITION(I2C_CheckEvent(I2C_EVENT_MASTER_MODE_SELECT),
        timeout_counter, I2C_TIMEOUT, return false);

    I2C_Send7bitAddress(I2C_SLAVE_ADDRESS << 1, I2C_DIRECTION_TX);
    BUSY_AWAIT_CONDITION(I2C_CheckEvent(I2C_EVENT_MASTER_TRANSMITTER_MODE_SELECTED),
        timeout_counter, I2C_TIMEOUT, return false);

    I2C_SendData(config);
    BUSY_AWAIT_CONDITION(I2C_CheckEvent(I2C_EVENT_MASTER_BYTE_TRANSMITTED),
        timeout_counter, I2C_TIMEOUT, return false);

    I2C_GenerateSTOP(ENABLE);
    return true;
}
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

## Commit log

2019-06-15 revision 4.0 (reworked git history)
    [DataAcquisition.sch, chamber.kicad_pcb, chamber.sch]
2019-06-16 added datalogger module, changed cpu id, added led
2019-06-29 raw setup on eclipse and raspberry
2019-06-30 Fixes after moving to target board
2019-06-30 draft of communication via LEDs
2019-07-03 uart used as printf output
2019-07-06 cleanup in sensors part
2019-07-13 added first image of the board
2019-07-14 fix #56 #74
    [DataAcquisition.sch, chamber.kicad_pcb, chamber.sch]
2019-07-14 fix #59 #71
    [DataAcquisition.sch, chamber.kicad_pcb, chamber.sch]
2019-07-20 updated docs for actual pcb version
2019-07-28 variant with and without printf
2019-08-04 updated device photo
2019-08-04 fix in communication pc vs device
2019-08-10 added flashing device after build
2019-08-16 fix #196
    [chamber.kicad_pcb, chamber.sch]
2019-08-16 fix #64
    [DataAcquisition.sch, chamber.kicad_pcb, chamber.sch]
2019-08-16 fix #197
    [chamber.kicad_pcb, chamber.sch]
2019-08-19 boxplot to analyze results between samples
2019-09-03 not mounted parts marked on diagram
    [DataAcquisition.sch, chamber.sch]
2019-09-03 fix #211
    [chamber.kicad_pcb, chamber.sch]
2019-09-07 aplied missing changes after hw assembly
    [DataAcquisition.sch, chamber.sch]
2020-05-30 added picture of the device to README.md
2020-10-22 Unify folder name convention with my other repos (first upper letter singular nouns)
    [DataAcquisition.sch, chamber.kicad_pcb, chamber.sch]
2021-07-03 add draft of pcb with high voltage supply and opamp power supply
    [DataAcquisition.sch, PowerSupply.kicad_pcb, PowerSupply.sch, chamber.kicad_pcb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]
2021-07-04 finished design of the power power supply pcb
    [PowerSupply.kicad_pcb, PowerSupply.sch]
2021-07-04 draft of sensor pcb
    [AnalogFrontend.sch, DataAcquisition.sch, Mechanic.sch, PowerSupply.kicad_pcb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]
2021-07-10 draft of routing of sensor
    [AnalogFrontend.sch, DataAcquisition.sch, Mechanic.sch, chamber.kicad_pcb]
2021-07-17 switched from stm32 nucleo to stm8, added user interface, added draft of pcb routing
    [AnalogFrontend.sch, DataAcquisition.sch, Mechanic.sch, UserInterface.sch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]
2021-07-18 finished pcb design
    [ADC.sch, AnalogFrontend.sch, DataAcquisition.sch, Mechanic.sch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]
2021-07-22 fix #249
    [chamber.kicad_pcb]
2021-07-24 added references to LCSC shop (for some components), slighty improved routing
    [ADC.sch, AnalogFrontend.sch, DataAcquisition.sch, UserInterface.sch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]
2021-07-25 fix #249, fix #251
    [PowerSupply.kicad_pcb]
2021-08-15 cleanup after transition to KiCad6
    [ADC.kicad_sch, ADC.sch, AnalogFrontend.kicad_sch, AnalogFrontend.sch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]
2024-08-17 this is what was send for pcb production
    [ADC.kicad_sch, AnalogFrontend.kicad_sch, DataAcquisition.kicad_sch, Mechanic.kicad_sch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]
2024-12-10 design of hw rev 6.0
    [ADC.kicad_sch, Amplifier.kicad_pcb, Amplifier.kicad_sch, AnalogFrontend.kicad_sch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]
2025-07-04 rework firmware, pc app, ci and docs
    [Amplifier.kicad_pcb, Amplifier.kicad_sch, DataProcessingUnit.kicad_pcb, DataProcessingUnit.kicad_sch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]
